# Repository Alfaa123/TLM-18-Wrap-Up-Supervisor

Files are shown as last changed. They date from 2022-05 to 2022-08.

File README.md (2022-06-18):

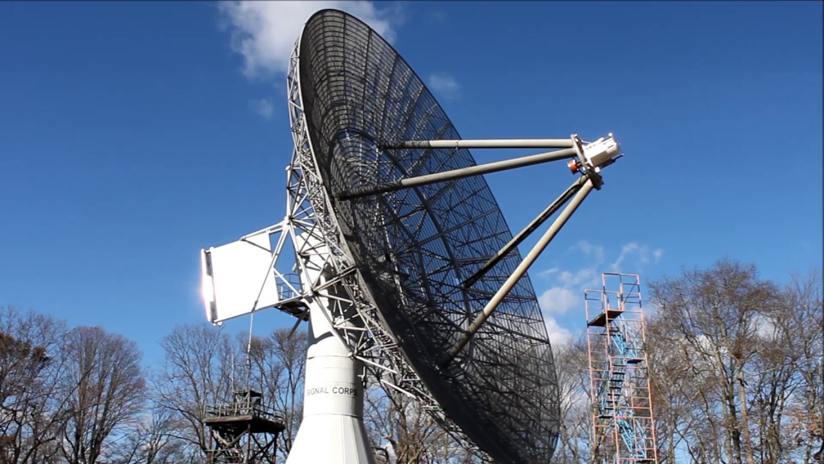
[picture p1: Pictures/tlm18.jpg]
TLM-18 Radio Telescope


# TLM-18-Wrap-Up-Supervisor
A monitor system to keep track of the number of consecutive 'wraps' the azimuth axis of the TLM-18 radio telescope has completed.

# This project is in progress, the following plan is being implemented:

A standard industrial quadrature encoder is attached to the selsyn shaft to monitor the position of the selsyn pinion.

400 pulses per revolution read in quadrature would give us 1600 PPR (0.225°) resolution at the selsyn pinion. The actual angular resolution of the azimuth axis would be further multiplied by the gear ratio of the pinion and ring gear.

A standard microcontroller would be used to read the quadrature outputs of the encoder and internally keep track of the position. A standard communications link (RS-232 or similar) would be used to communicate the current position back to the computer at specified intervals.

In order to keep track of the position of the telescope during power loss, a small battery backup system will be used to maintain power to the microcontroller during all conditions. Due to the minimal power consumption of the microcontroller/encoder combination, a small lead acid deep cycle battery should be able to maintain power to that system for many hours.

An additional feature that could be implemented is additional sensors to monitor environmental conditions inside the telescope. Temperature and humidity could be logged, as well as a small Inertial Measurement Unit to detect abnormal vibration in the positioning system. Additional sensing capabilities would allow a remote user to detect issues before they get too out of control.

Physically, the electronics would be mounted in a weatherproof enclosure attached somewhere near to the selsyn pinion to keep the encoder wire as short as possible.

# Electrical Design

The TLM-18 Supervisor system is controlled by an Arduino Nano as the main MCU. This was chosen for ease of software development, ubquity and cost.

The entire system is powered by a small 12v lead acid battery float charger connected to a standard 12v UPS battery. This gives the system a short battery backup supply should mains power be inturrupted.

Attached to the Arduino is an LS7366R SPI Encoder Counter to keep track of the encoder pulses. This will allow high PPR encoders without overwhelming the inturrupt capability of the Arduino at high speeds.

A ADM488ANZ RS-422 transceiver is also attached to allow long distance and isolated communication with the TLM-18 control computer, which will be located a significant distance away and may not be at the same ground potential.

The schematic and board layout are shown below:

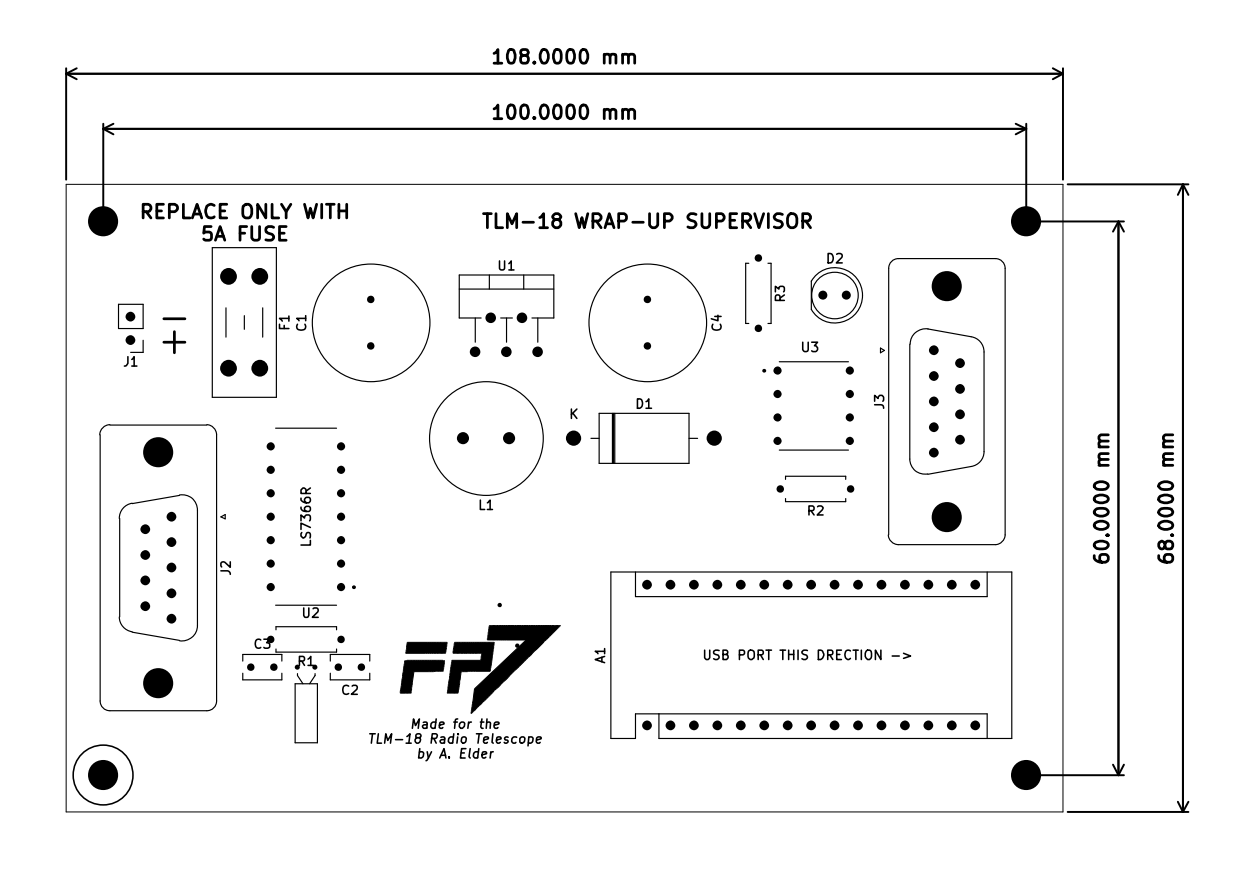
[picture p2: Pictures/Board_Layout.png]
Board Layout

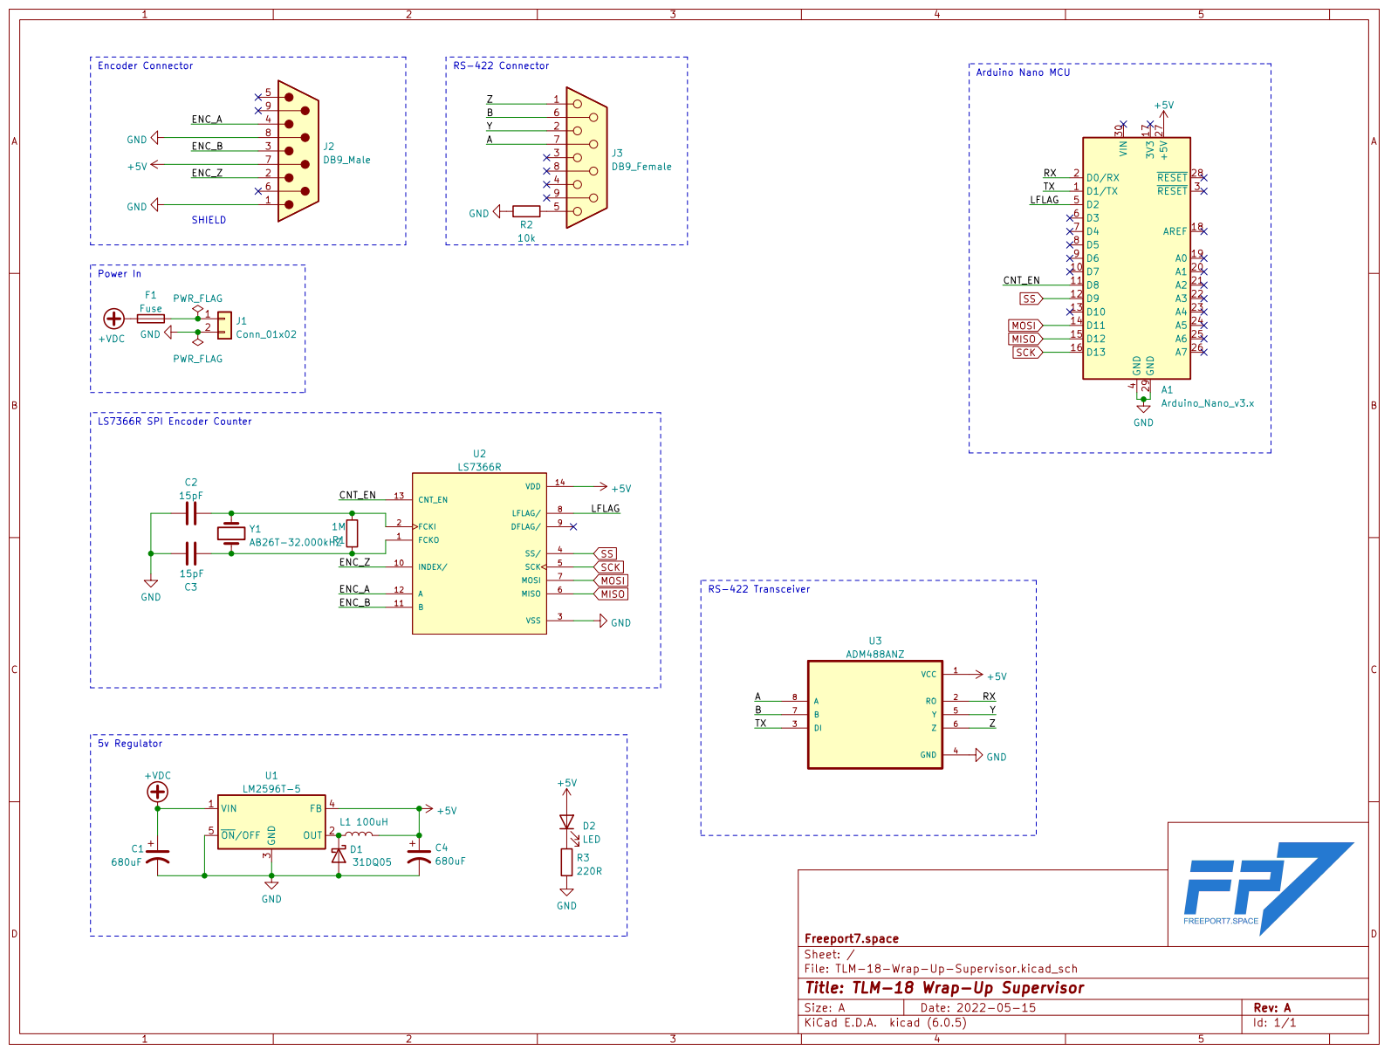
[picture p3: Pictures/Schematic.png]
Board Schematic


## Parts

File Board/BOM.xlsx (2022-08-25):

Item | Part Number | Vendor | Quantity | Price | Extended Price | Link
Items for 1 PCB
Serial Encoder Counter | LS3766R | DigiKey | 1 | $6.62 | $6.62 | https://www.digikey.com/en/products/detail/lsi-csi/LS7366R/12760871
RS422 Transceiver | ADM488 | DigiKey | 1 | $4.33 | $4.33 | https://www.digikey.com/en/products/detail/analog-devices-inc/ADM488ANZ/1007310
Crystal Oscillator | ACH-25.000MHZ-EK | DigiKey | 1 | $2.61 | $2.61 | https://www.digikey.com/en/products/detail/abracon-llc/ACH-25-000MHZ-EK/675370
DC Buck Converter | LM2596T-5.0 | DigiKey | 1 | $6.12 | $6.12 | https://www.digikey.com/en/products/detail/texas-instruments/LM2596T-5-0-LF03/3640657
Schottky Diode | 31DQ05 | DigiKey | 1 | $0.39 | $0.39 | https://www.digikey.com/en/products/detail/smc-diode-solutions/31DQ05TA/12142429
680uF Capacitor | 50PX680MEFC12.5X20 | DigiKey | 2 | $0.92 | $1.84 | https://www.digikey.com/en/products/detail/rubycon/50PX680MEFC12-5X20/3134365?s=N4IgTCBcDaIIxwBwE4C0cAsAGNA5AIiALoC%2BQA
100uH Inductor | 7447471101 | DigiKey | 1 | $2.54 | $2.54 | https://www.digikey.com/en/products/detail/w%C3%BCrth-elektronik/7447471101/3476776
Fuse Holder | 3568 | DigiKey | 1 | $1.33 | $1.33 | https://www.digikey.com/en/products/detail/keystone-electronics/3568/2137306
Power Connector | OSTVN02A150 | DigiKey | 1 | $0.96 | $0.96 | https://www.digikey.com/en/products/detail/on-shore-technology-inc/OSTVN02A150/1588862
DB-9 Male | A-DS 09 PP/Z-BK | DigiKey | 1 | $0.70 | $0.70 | https://www.digikey.com/en/products/detail/assmann-wsw-components/A-DS-09-PP-Z-BK/10668847
DB-9 Female | A-DF 09 PP/Z-BK | DigiKey | 1 | $0.71 | $0.71 | https://www.digikey.com/en/products/detail/assmann-wsw-components/A-DF-09-PP-Z-BK/10668849
Items for Mechanical Assembly
DB-9 Connector Assortment |  | Amazon | 1 | $16.99 | $16.99 | https://www.amazon.com/ANMBEST-Connector-Terminal-Breakout-Assortment/dp/B09698YCTZ/?th=1
1000 PPR Rotary Encoder | RE30E-1000-213-1 | DigiKey | 1 | $96.21 | $96.21 | https://www.digikey.com/en/products/detail/nidec-copal-electronics/RE30E-1000-213-1/6469499
Isolated USB RS422 Interface |  | Amazon | 1 | $20.99 | $20.99 | https://www.amazon.com/DSD-TECH-SH-U11F-Industrial-Application/dp/B083XSG1RG/
 |  |  |  | Total Price | $162.34

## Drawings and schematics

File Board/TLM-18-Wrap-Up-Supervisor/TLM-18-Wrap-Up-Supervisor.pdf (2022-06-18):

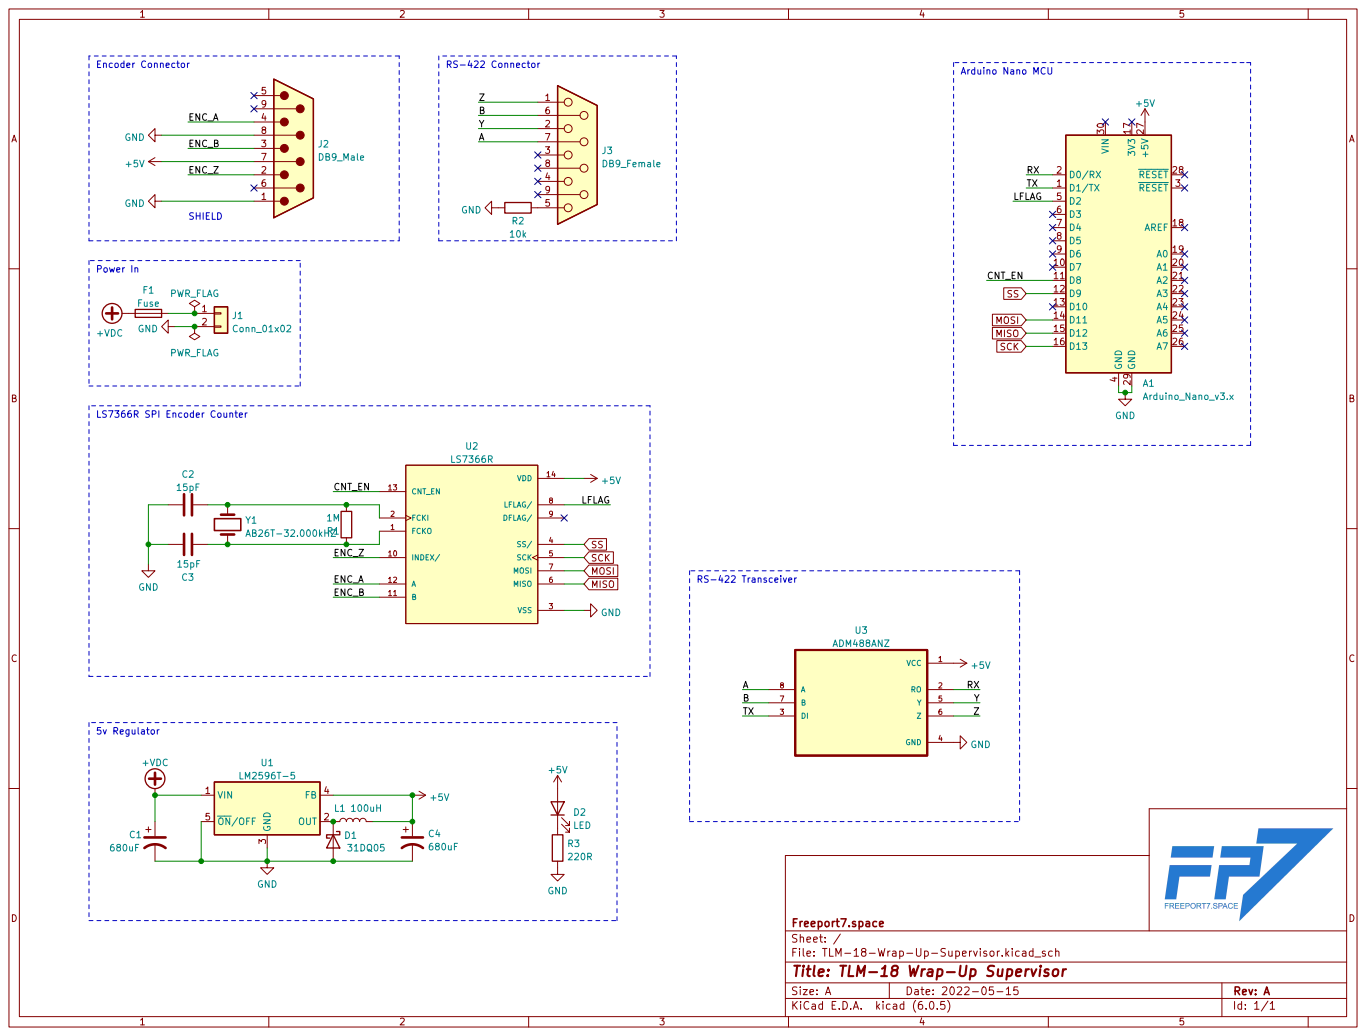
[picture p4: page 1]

LS7366R SPI Encoder Counter Power In

File: TLM-18-Wrap-Up-Supervisor.kicad_sch Sheet: / Freeport7.space

Id: 1/1 Title: TLM-18 Wrap-Up Supervisor

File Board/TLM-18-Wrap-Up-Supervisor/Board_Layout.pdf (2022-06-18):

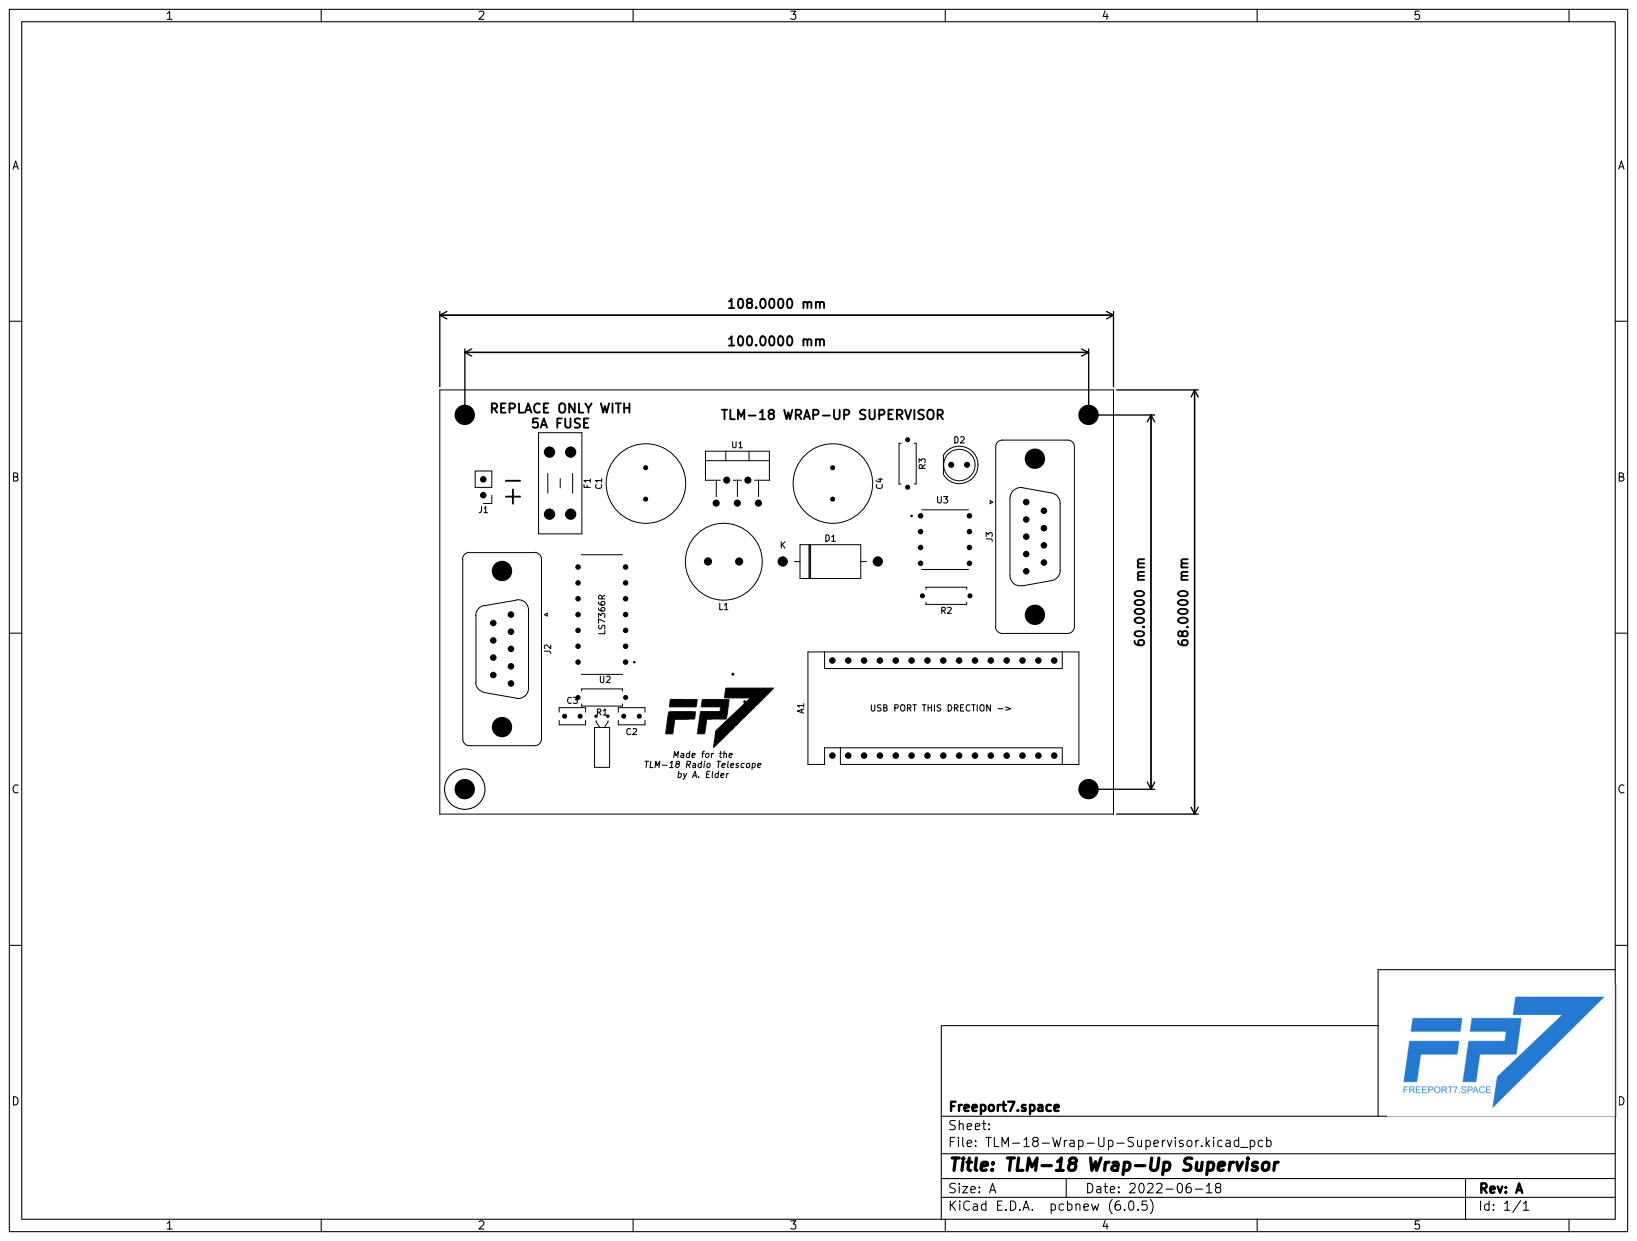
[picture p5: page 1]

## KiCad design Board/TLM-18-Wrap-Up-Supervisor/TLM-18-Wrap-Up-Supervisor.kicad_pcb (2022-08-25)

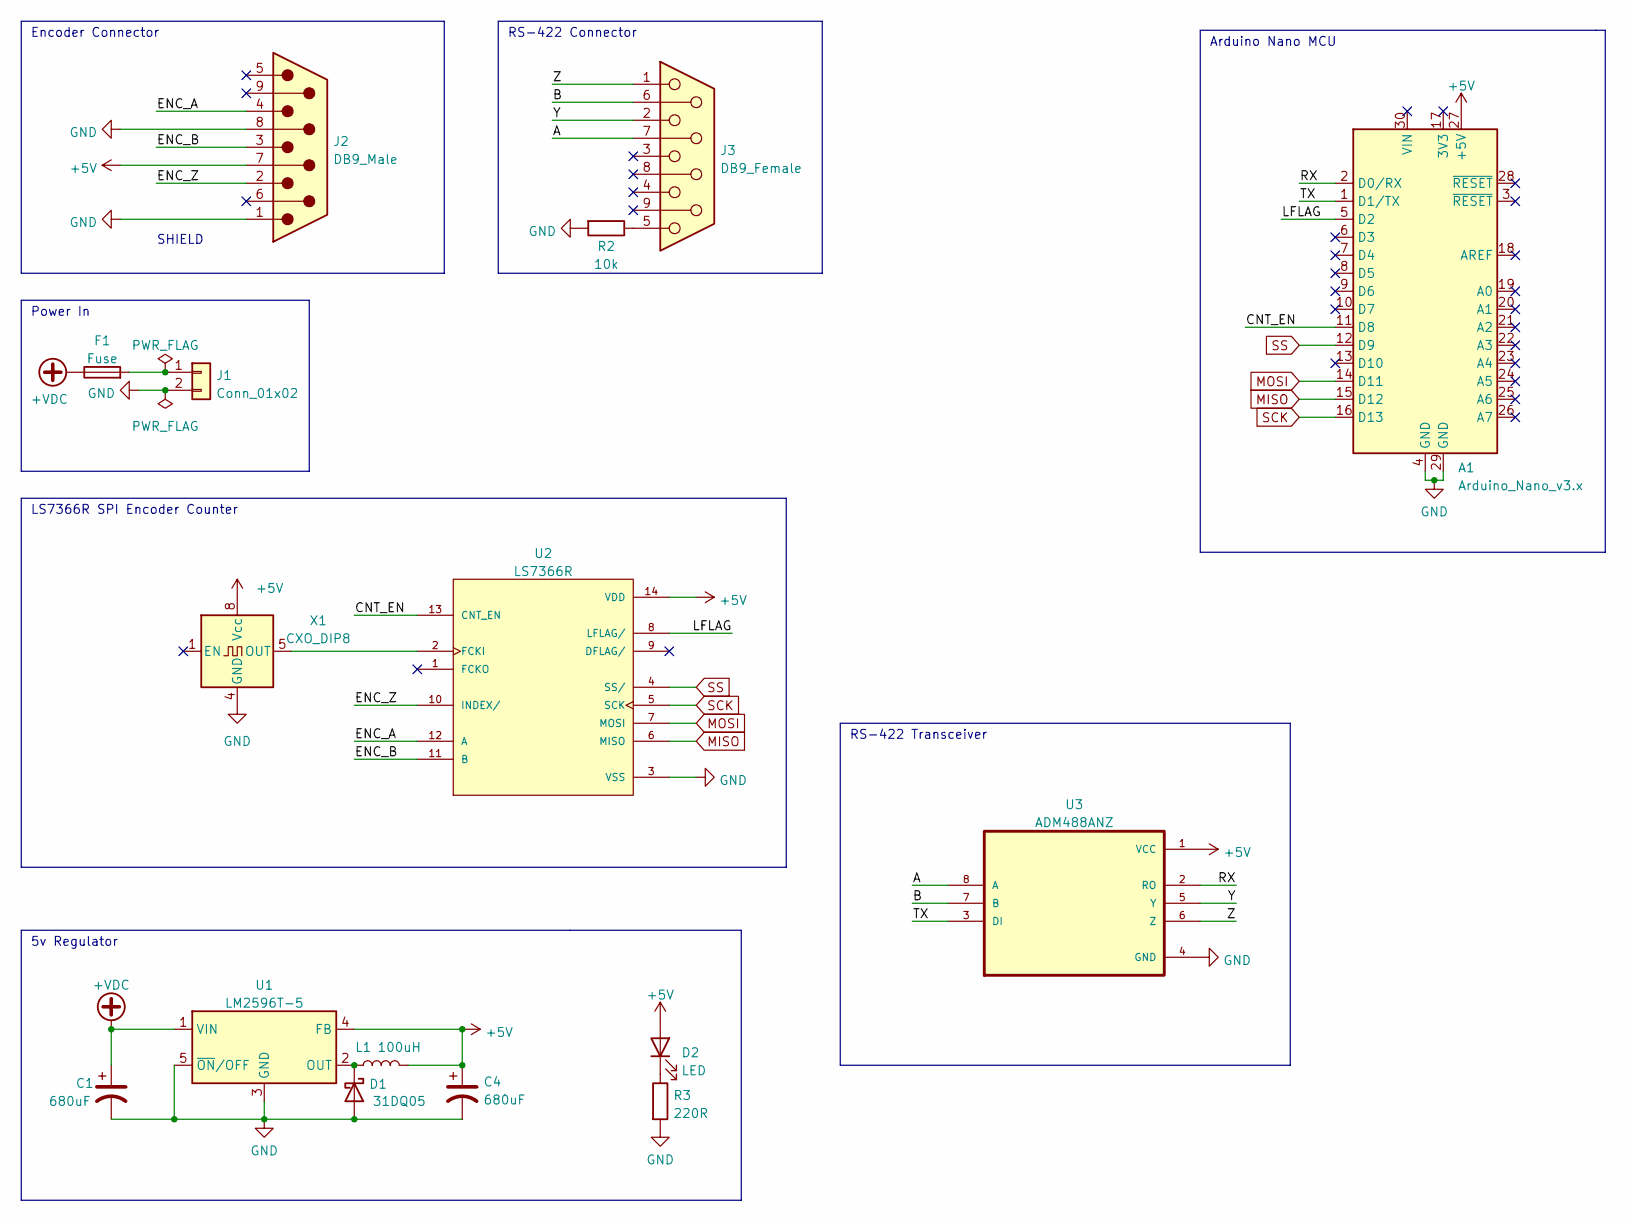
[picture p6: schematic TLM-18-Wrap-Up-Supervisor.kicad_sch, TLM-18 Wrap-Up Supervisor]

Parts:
A1: Arduino_Nano_v3.x; Arduino_Nano
C1, C4: 680uF; C_Radial_D12.5mm_H20.0mm_P5.00mm
D1: 31DQ05; D_DO-201AD_P15.24mm_Horizontal
D2: LED; LED_D5.0mm
F1: Fuse; Fuseholder_Blade_Mini_Keystone_3568
J1: Conn_01x02; PinHeader_1x02_P2.54mm_Vertical
J2: DB9_Male; DSUB-9_Male_Vertical_P2.77x2.84mm_MountingHoles
J3: DB9_Female; DSUB-9_Female_Vertical_P2.77x2.84mm_MountingHoles
L1: 100uH; L_Radial_D12.0mm_P5.00mm_Fastron_11P
R2: 10k; R_Axial_DIN0207_L6.3mm_D2.5mm_P7.62mm_Horizontal
R3: 220R; R_Axial_DIN0207_L6.3mm_D2.5mm_P7.62mm_Horizontal
U1: LM2596T-5; TO-220-5_P3.4x3.7mm_StaggerOdd_Lead3.8mm_Vertical
U2: LS7366R; DIP762W45P254L1917H533Q14; PARTREV June 2014
U3: ADM488ANZ; DIP787W46P254L953H457Q8
X1: CXO_DIP8; Oscillator_DIP-8

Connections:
+5V: A1.27 (+5V), C4.1, D2.2 (A), J2.7, L1.2, U1.4 (FB), U2.14 (VDD), U3.1 (VCC), X1.8 (Vcc)
+VDC: C1.1, F1.1, U1.1 (VIN)
/A: J3.7, U3.8 (A)
/B: J3.6, U3.7 (B)
/CNT_EN: A1.11 (D8), U2.13 (CNT_EN)
/ENC_A: J2.4, U2.12 (A)
/ENC_B: J2.3, U2.11 (B)
/ENC_Z: J2.2, U2.10 (INDEX/)
/LFLAG: A1.5 (D2), U2.8 (LFLAG/)
/RX: A1.2 (D0/RX), U3.2 (RO)
/TX: A1.1 (D1/TX), U3.3 (DI)
/Y: J3.2, U3.5 (Y)
/Z: J3.1, U3.6 (Z)
GND: A1.4 (GND), A1.29 (GND), C1.2, C4.2, D1.2 (A), J1.2, J2.1, J2.8, R2.2, R3.2, U1.3 (GND), U1.5 (~ON/OFF), U2.3 (VSS), U3.4 (GND), X1.4 (GND)
MISO: A1.15 (D12), U2.6 (MISO)
MOSI: A1.14 (D11), U2.7 (MOSI)
unnamed: D1.1 (K), L1.1, U1.2 (OUT)
unnamed: D2.1 (K), R3.1
unnamed: F1.2, J1.1
unnamed: J3.5, R2.1
unnamed: U2.2 (FCKI), X1.5 (OUT)
SCK: A1.16 (D13), U2.5 (SCK)
SS: A1.12 (D9), U2.4 (SS/)

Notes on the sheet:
RS-422 Connector
Arduino Nano MCU
LS7366R SPI Encoder Counter
Power In
Encoder Connector
SHIELD
RS-422 Transceiver
5v Regulator

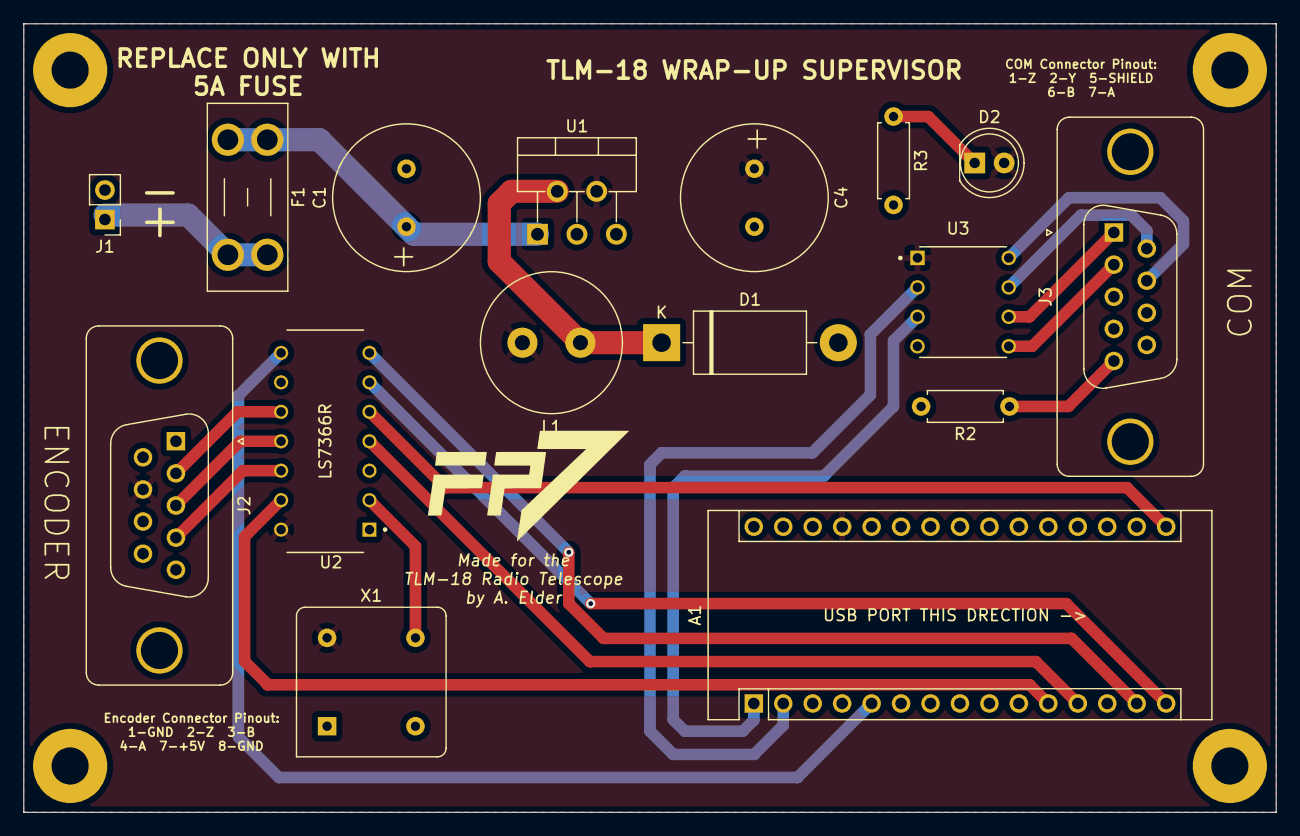
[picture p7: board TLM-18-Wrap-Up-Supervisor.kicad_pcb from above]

Board: 2 copper layers, 108.0 x 68.0 mm, 16 parts (0 on the bottom side), 23 nets.

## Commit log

2022-05-15 Version 1 of the Schematic Finished
    [BOM.xlsx, TLM-18-Wrap-Up-Supervisor.kicad_pcb, TLM-18-Wrap-Up-Supervisor.kicad_sch, TLM-18-Wrap-Up-Supervisor.sch]
2022-06-18 Added photos, finished board layout, updated readme
    [BOM.xlsx, TLM-18-Wrap-Up-Supervisor-B_Cu.gbr, TLM-18-Wrap-Up-Supervisor-B_Mask.gbr, TLM-18-Wrap-Up-Supervisor-B_Paste.gbr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]
2022-08-25 Updated board SS + BOM
    Changed crystal to prepackaged oscillator, added extra silkscreen marks
    [TLM-18-Wrap-Up-Supervisor-B_Cu.gbr, TLM-18-Wrap-Up-Supervisor-B_Mask.gbr, TLM-18-Wrap-Up-Supervisor-B_Paste.gbr, TLM-18-Wrap-Up-Supervisor-B_Silkscreen.gbr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]
